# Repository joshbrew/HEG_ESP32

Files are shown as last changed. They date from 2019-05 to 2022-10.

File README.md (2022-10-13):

# HEG ESP32 - Open Source. Home of HEGduino!
Hemoencephalography meets highly affordable IoT! Now with WiFi and bluetooth! Incoming schematics, apps, and how-to's. [New Delobotomizer repo here](https://github.com/moothyknight/HEG_ESP32_Delobotomizer) for drivers for the new hardware.

Find the new, vastly easier to assembly HEGduino_V0 (3 parts, <10 dollars): https://github.com/joshbrew/hegduino_v0

Important HEGduino stuff you can find here:
- [HEG Training Quick Start Guide](https://github.com/moothyknight/HEG_ESP32/blob/master/Guides/HEG%20Training%20Quick%20Start%20Guide.pdf)
- [Progressive webapp (WIP) for Desktop or Android. Use with Chrome for now](https://hegalomania.netlify.app)
- [HEGduino Assembly](https://github.com/moothyknight/HEG_ESP32/blob/master/Guides/HEGduino%20Assembly%20Guide.pdf)
- [(For self-assembly only) Setting up Arduino to flash the ESP32 with our biofeedback software](https://github.com/moothyknight/HEG_ESP32/blob/master/Device_README.txt)
- [Updating the firmware via the web interface](https://github.com/moothyknight/HEG_ESP32/blob/master/Guides/How%20To%20Update.pdf)
- [Lolin32 Firmware and Updates](https://github.com/moothyknight/HEG_ESP32/tree/master/Device%20Drivers/HEG_WIFI_BLE_Lolin32)
- [Huzzah32 Feather Firmware and Updates](https://github.com/moothyknight/HEG_ESP32/tree/master/Device%20Drivers/HEG_WIFI_BLE_Feather)

## What is it?
Hemoencephalography is a single sensor FNIRS device meant to give a basic indication of cerebral blood flow changes in the brain.
Users then combine this indicator - the ratio of red to infrared light returned to the photodiode from the LEDs on your scalp or forehead - with simple visualization tools to help them increase or decrease metabolic/blood flow activity in the brain. 
This works like an odd form of physical therapy and is implicated as a powerful tool when combined in any brain health related therapies.

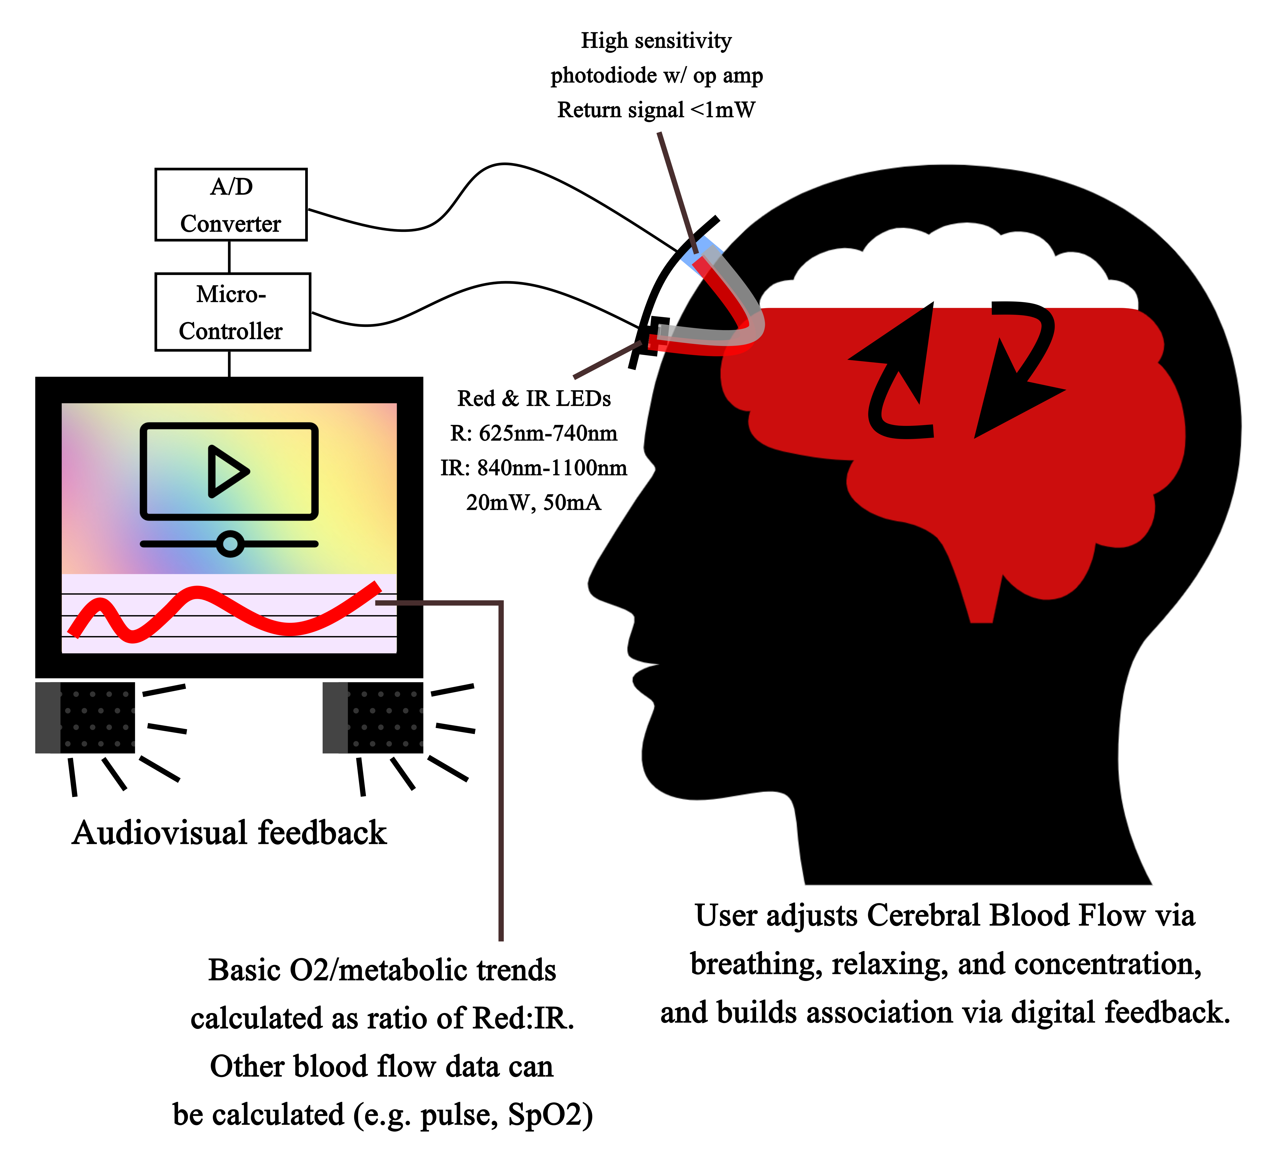
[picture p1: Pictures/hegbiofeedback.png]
Explanation


## Software

### Arduino Setup
See the [Device_Readme.txt](https://github.com/moothyknight/HEG_ESP32/blob/master/Device_README.txt)  for flashing instructions as well as available USB/WiFi/BLE commands and the changelog, including which dependencies are required for the Arduino IDE. We packaged the more minor dependencies in the Device_Drivers folder so you don't have to chase all of them down, just get Arduino and the ESP32 addon (github version) working.

Use the HEG_WIFI_BLE sketch in the arduino IDE on your respective ESP32. Pin definitions in HEG.h for the SDA/SCL and LEDs need to be adjusted according to your setup. 

These builds are tested on the Lolin32 and Huzzah32 Feather respectively but should work on any board after modifying the pinouts in HEG.h

### All Open Source Games, Tools, & APIs. See [the new PWA!](https://hegalomania.netlify.app)

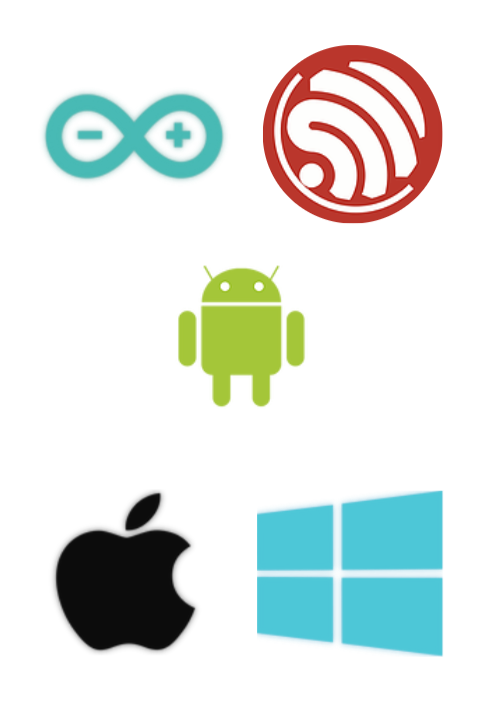
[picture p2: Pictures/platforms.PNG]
platforms


On the firmware you will find a Async Web Server with a cross-platform supported javascript app, enabling plug-and-play and global networking features. We are creating an open source combined therapy and research toolset, using the perks of an online-enabled device and all of the diverse tools available for web front and backend. This is a living project so stay tuned!

You can demo it now at a new mobile or desktop-installable webapp at [hegalomania.netlify.app](https://hegalomania.netlify.app). 

The USB support on the PWA is chrome-only until it is out of development for default web support. Install on desktop by opening the setting dropdown in Chrome (the 3 vertical dots in the top right of the browser) and click "Install HEG Alpha." It should be kept up to date automatically and work offline. Make sure you have the Earth textures on the Sunrise mode cached to use them offline, simply load them once to do this.  

It's evolving fast. We will eventually be comparable to professional BCI software, free of charge. In the More folder, please find the DataCharting.html applet for analyzing and comparing your data with interactive charts.

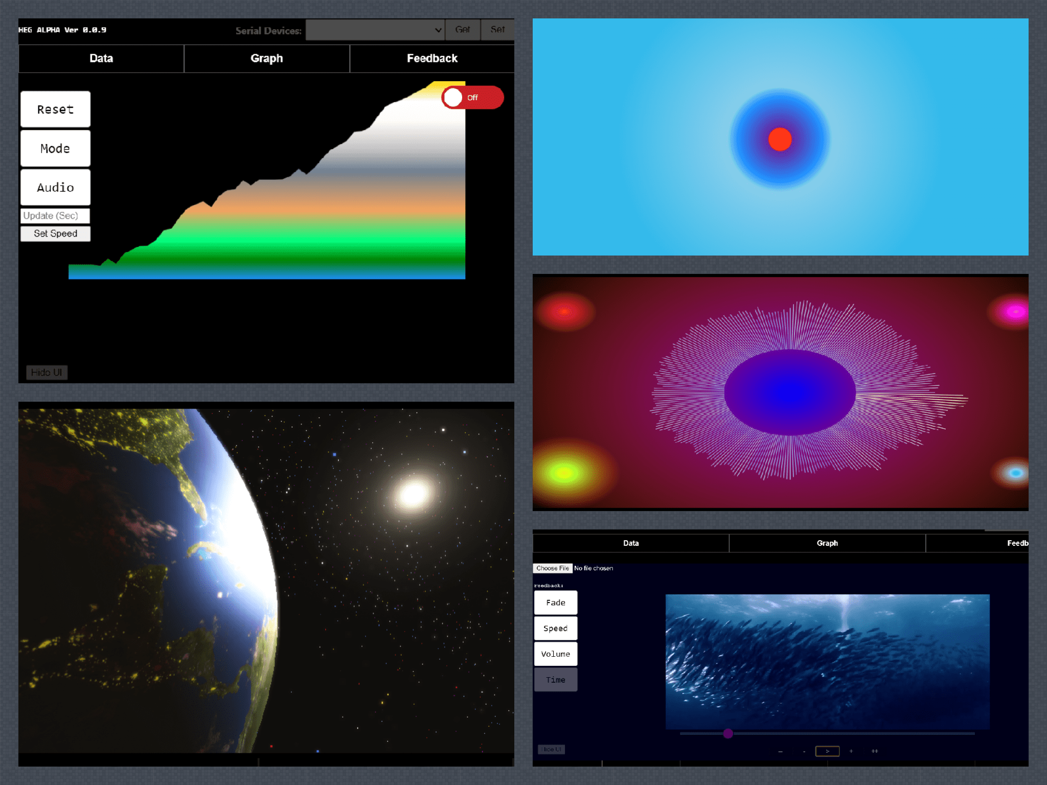
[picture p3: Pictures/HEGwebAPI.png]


## Data Charter (To be replaced) CSV analyzer for the web app (also found on our [Data page on our website](https://hegalpha.com))
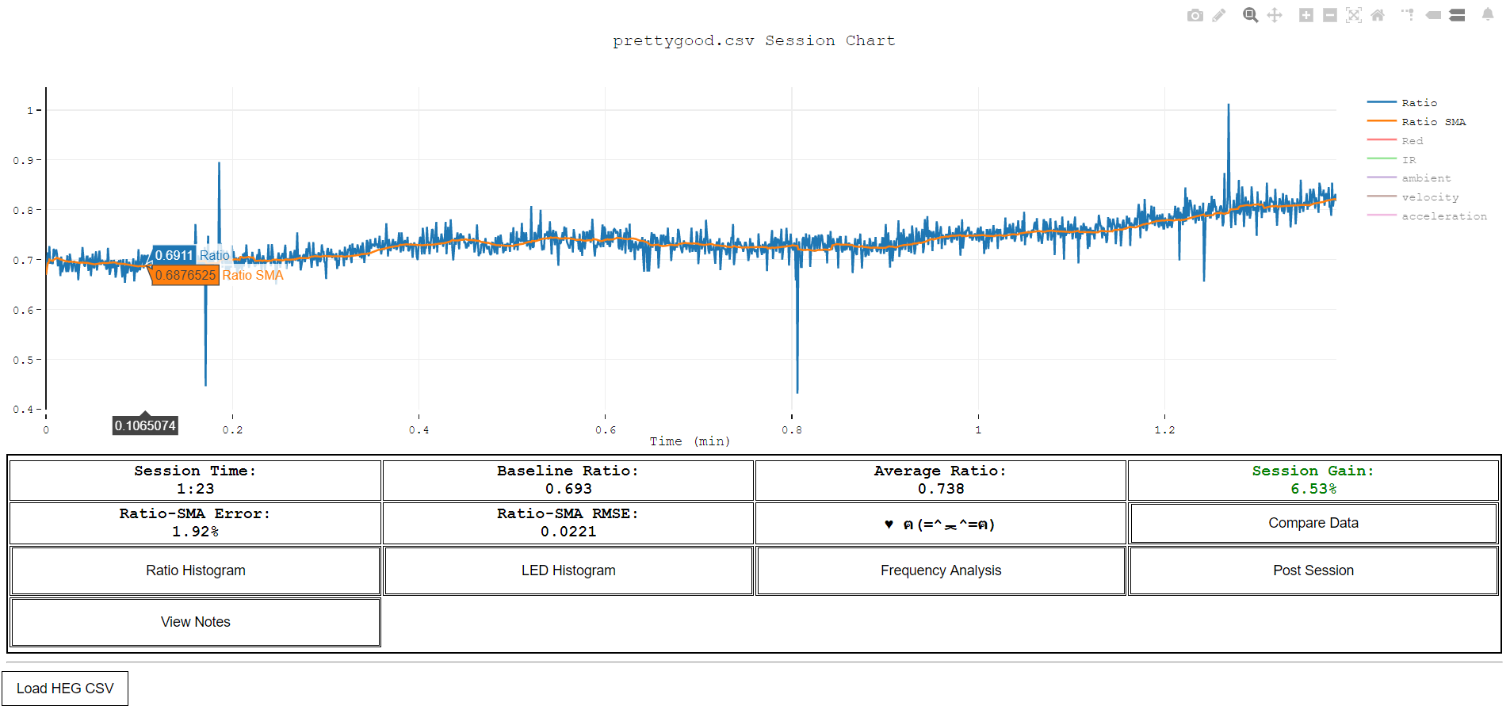
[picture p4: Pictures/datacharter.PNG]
HEGCharter


## More Links
Our website: [HEG Alpha](https://hegalpha.com)

Find us on [CrowdSupply](https://crowdsupply.com/alaskit/hegduino)

and [OpenBCI](https://shop.openbci.com/collections/frontpage/products/hegduino-kit?variant=32052268531784)

Special thanks to the [Biocomp/Biofeedback Institute of LA](https://www.biocompresearch.org/), [Brain Trainer](https://brain-trainer.com/), and [AlasKit](https://alaskit.net)

See also (very deprecated):
[Arduino Nano V3 HEG](https://github.com/moothyknight/HEG_Arduino)

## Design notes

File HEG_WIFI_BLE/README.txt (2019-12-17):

HEG WiFi WIP implementation. 

*****TO FLASH THIS SKETCH*****

You need the github version of the Arduino ESP32 libraries, follow steps accordingly for your OS.

You need to change the partition scheme to "Minimal SPIFFS" in the Arduino Tools menu.

Required Libraries: 
Arduino ESP32 latest dev or official build via git
AsyncTCP 
ESPAsyncWebServer 
ADS1X15
ArduinoJson

*****
IMPORTANT STEP
In Documents/Arduino/hardware/espressif/esp32/cores/esp32, open main.cpp and change 
xTaskCreateUniversal(loopTask, "loopTask", 8196, NULL, 1, &loopTaskHandle, CONFIG_ARDUINO_RUNNING_CORE);
to
xTaskCreateUniversal(loopTask, "loopTask", 16384, NULL, 1, &loopTaskHandle, CONFIG_ARDUINO_RUNNING_CORE);
The heap memory needs to be increased as the change in wifi can be too much on for the default arduino config. 
*****

After flashing this sketch onto the ESP32, you will find the new wifi
access point at the SSID: My_HEG with password: 12345678.

After logging into the access point, access the interface at 192.168.4.1

********************************

**
Optional - to have increased SPIFFs:

Arduino's default partition settings for the ESP32 need to be changed. A shell script has been provided to speed this up.

In the Arduino>hardware>espressif>esp32 folder replace boards.txt with the one in this library

In esp32>tools>partitions replace default.csv with the one in this library

These change the default partitioning to allow sketches up to 2MB in size on the ESP32 to make room for dual WiFi and BLE.

Extra SPIFFS notes:
You need the SPIFFs tools: https://github.com/me-no-dev/arduino-esp32fs-plugin
You also need to copy the esptool and mkspiffs EXE files in Arduino/hardware/espressif/esp32/tools/esptool and .../tools/mkspiffs into the
upper .../tools directory so the SPIFFs tool can find them.
**

--DEVICE INSTRUCTIONS--

HEG serial commands:
't' - Turns sensor on, you'll see a data stream if the sensor is isolated, as in contacting your skin and not exposed to ambient light.
'f' - Sensor off.
'W' - Reset WiFi to default access point mode (wipes saved credentials).
'b' - Toggle BLE mode, this resets the device to start in BLE mode, so you have to enter 'b' again through the serial or BLE connection to switch back to WiFi.
'R' - hard resets the ESP32.
's' - soft resets the sensor data.
'u' - toggles USB data stream. 
'p' - really basic pIR setting. Just turns the LEDs off as the photodiode picks up radiant heat from your body.
'0','1','2','3' - Changes ADC channel the device reads, in the case of multiple light sensors.
'5' - Read differential between A0 and A1 on ADS1115 to reduce noise (e.g. connect A1 to signal ground).
'6' - Read differential between A2 and A3 on ADS1115.
'D' - toggles ADC debugging (serial only).
'L' - toggles LED ambient light cancellation .
'T' - LED/PD test function. Not finished, easier to just check the 't' output real quick.
//'A' - BUGGED - toggles ADC error catching (if experiencing major fluctuations in data)

With extra sensors:
'l' - toggles sensor 0 and LED set 0.
'c' - toggles sensor 0 and LED set 2.
'r' - toggles sensor 1 and LED set 3.
'n' - broken and basic noise reduction implementation, where two LED sites are compared. This is not a good implementation yet, may cause device to hang.

Output data stream:

Current Milliseconds | Red LED Sample Average | IR LED Sample Average |
Red/IR Ratio Average | small Sav Lay Filter | large Sav Lay Filter |
adc Avg | position Average | ratio Slope | Attention Index

With noise average activated, the denoised ratio (if using an extra pair of LEDs) is inserted between Red/IR Ratio Avg and the small Sav Lay Filter.

The following demo pages are available:
/       - Index page, basic site navigation.
/sc     - State Changer demo page.
/listen - HEG Output event listener test. Better than websockets for this use case.
/connect - connect HEG to router so it may be accessed via a router instead. 
/update - Upload compiled binaries and flash the ESP32 over the web.

-------

Wifi code notes:

Use the /connect page to save Wifi credentials to EEPROM. The ESP32 will reset and attempt connection. 
If connection fails, the access point opens (StateChanger in your WiFi scanner).

BLE and WiFi do not work concurrently at the moment, logging into WiFi with BLE enabled may cause the ESP32 to crash.
Use the serial 'b' command for now to test switching modes or use the /connect page options.

mDNS should allow the ESP32 to be accessed via http://esp32.local. It requires Bonjour service enabled. I have not had success yet, but it works on Apple systems apparently.

-------

Serial Port notes:
Chrome app serial monitor (alternative to Arduino): https://chrome.google.com/webstore/detail/serial-monitor/ohncdkkhephpakbbecnkclhjkmbjnmlo/related?hl=en
Arduino IDE has a debugger that comes with the ESP32 libs if there are some weird crashes happening.
-------

HEG Code notes:

The noise_reduce() function in this version is still broken. That needs to be triggered.

On the /listen or /stream page once the event listener/websocket is connected you can control and test the HEG through the Serial monitor. Right now there is a manual 75ms delay on the data stream, I'm going to create buffers as the new sensors will be WAY faster than TCP can handle.

*-*-*-*-*-*-*
Changelog:
*-*-*-*-*-*-*
12/16/19
------
- updated front page, connection page, and help page. Now with version number visible on main page.
- the web API lets you set an arbitrary host for the event source now for quicker remote play (set host with a new HEGwebAPI(parentId,defaultUI,**hostIP**))
 
12/14/19
------
- Made standalone /api page with uninitialized JS api and CSS available for external use.

12/10/19
------
- Rolled back ADC library due to too much instability.

12/8/19
------
- Fixed sampling issues. Now doing 3 samples per LED (and ambient) for 20sps solid over USB, WiFi, and BLE.
- Fixed BLE (thanks Diego!)

12/3/19
------
- Changed ADS1115 libraries to the addicore version (via on i2cdevlib)
- Upped sample rate to 475sps, ratio rate (with ambient cancellation) should now be ~133 at full speed over Serial.
- Fixed Serial commands not being responsive
- Removed "T" test command for now.

11/25/19
------
- fix LEDs not shutting off when pausing HEG
- lowered power consumption
- fixed circleJS in web API

Known bugs:
- Serial USB commands don't register very well 
- ADC anomalies with WiFi (probably power consumption related)
- xOffset bugged when changing xScale and xOffset together

To Do:
- Use a better ADS1115 lib to improve speed
- Web Demo CSS and functionality improvements
- IE and Edge can't find the HEGwebAPI.js script (this is likely the same issue on mobile)

11/11/19
------
- fix web api and hegstudio to match changes

11/9/19
------
- removed sav lay filter (do it on front end instead after checking data)

11/4/19
------
- ADC error check in HEG.h (to deal with a webserver bug), use 'A' to toggle. 
- Add progress events for /update page.

KNOWN BUGS:
The error checker can cause hangups and overheat the chip, don't use it yet

11/3/19
------
-webDemo now filters bad data out for a smoother experience, to compensate for a bug mainly
-testing threading to try to fix wifi data streaming errors. Turn sensor off and on if connecting online while sensor is active. (very particular not often-gonna-happen bug)

Known bugs:
The wifi connection causes errors in the ADC readings for some reason, need to fix this
to make the sav lay filters usable over web.

10/29/19
------
-/discovery page for testing device scanning from mobile
-Reimplemented ambient noise cancelling and added a read_differential mode. Works much better like this, closer to the original!
-/help page (BIG work in progress)

10/21/19
------
-connect page now has a suggest IP option. Return to the /connect page after reconnecting to the access point.
If it works correctly you get booted to the main page and can go straight to the /connect page again, scroll down, and see the suggested info above the wifi scan text.
-proof of concept hill climb game
-more cleanup (not all the way there yet)

More to do:
Audio mode that just plays a tone that gets louder or quieter? 
Device search on local wifi when in STA mode.
More controls for modes.

10/18/19
------
-integrated audio mode
-added volume feedback for video option
-code feng shui improvements

FYI: not all buttons hooked up yet

Known bugs:
-not every browser works on canvas demo
-poor audio quality on visualizer mode - try manual buffering. Bug not present in standalone visualizer.
-offset button bugged when offsetting more than the number of graph vertices (look at xoffsetSlider.onclick setting)
10/17/19
------
smooth mode switching on demo page. Audio and hill climbing (LIFE game re-creation) games incoming.
change graph to show cumulative SMA 1s - 2s slope changes. This math is a simple noise filter that is still reactive to the current information, which can overcome noise issues. 
split code up into multiple files to fit a cleaner traditional webapp format.
web api improving and generalizing rapidly
can set primary/secondary dns if needed, smart config type stuff incoming.

couple bugs:
X offset slider still, it's 3 lines of code causing a problem.
the replay function works fine but goes over the index when resetting the data. This bit will be re-done as the code is spaghetti.

10/14/19
------
-x offset bar. Has a bug when offsetting when graph scale is lower than the array being sliced. page has to be reloaded if red line vanishes.
-Even classier, almost finished streamlining code.
-integrated hegvid code with main page, need to create options to swap once finished generalizing the data handling. this will be smoooooth

10/13/19
------
webGL graphing API improvements. More to come.
WIP Object-oriented web API on canvas demo page. Final suite will be completely class-based.
Sensitivity slider.
/hegvid -> /video (this page will be integrated with the main demo)

More TODO:
Audio visualizer (HTML5 has sweet built-in tools)
CSS Overhaul w/ animations. Utilize webkit/moz/mobile libs.
Fix mobile support for web demo (mostly requires permissions changes)

10/11/19
-----
/hegvid page improvements/experiments. Can load local video files (web URLs next, some site embedding like Vimeo MIGHT work)

10/10/19
-----
CSV Save/Load functions added.
Graphing improved, canvas demo fairly playable now. 
Waiting on new pcbs to get definitive data after fixing noise issues in designs.
GraphJS wrapper class for graphing.

TODO:
graph upgrades
reformat functions and variables into respective classes to reduce bloat.
sliders for exploring data
create SPIFFS js packages? That way we can break up essential functions on the webAPI and reduce bloat or add third party packages easily.
hegstudio brightness exercise recreation is easiest to do with default <video> tag and a transparency overlay.
Fix spaghetti

10/6/19
-----
Fixed crash when changing wifi modes
Add static IP settings. 
Working on WebGL based graphing and video controls. /hegvid wip

10/1/19
------
Canvas demo
Really basic navigation on index page
Fix websocket page to use js to call the hostname in case of esp32.local being used.
More POST commands, also added text input-based command method as an option, only send single char.

9/9/19
------
EventSource works great!

More TODO:
Make connect page notify the user of the new IP address if esp32.local is not fixed.
Convert websockets to drive commandESP32

9/5/19
------
TODO:
Data visualizer. HEG Life game in canvas?
Stress testing - try EventSource instead of Websockets. Websockets can overflow and crash the ESP32 easily if there is lag clientside.
Login interface?
HTML interface to use commandESP32

9/5/2019
------
Fixed OTA, update boards.txt and default.csv in their respective folders (see above install instructions)
Changed setup loop so wifi is always chosen if EEPROM.read(0) is not 1 for BLE.

9/3/19
------
Included BLE support. toggle BLE/WIFI with 'b', BLE default off due to conflict with WiFi
Websockets and HEG now on separate threads so sensor speed is not impacted - WS speed set at 13.33 updates/sec as it's stable. Max = 16/sec
/update broken. Gotta fix it.
Lots of housekeeping to keep workflow easy, tested the freeRTOS threading system a ton.
commandESP32 now in WiFi_API.h.

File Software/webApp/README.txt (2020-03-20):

Step 1: Connect to your HEG WiFi
Step 2: Open webDemo.html (preferably with Chrome, Firefox, Edge Beta, or Brave) and open the Data menu
Step 3: Click "Connect" to connect to 192.168.4.1 or enter a custom IP if you are connected through a network.
Step 4: Press start! You should see your device come on!

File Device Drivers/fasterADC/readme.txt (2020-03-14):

You can replace your HEG.h and WiFi_API.h with these as well as add the library to your Arduino Libraries folder.

To get the ADS1115 library working (use the addicore version on github), you must also have the I2C device library by jrwoberg.
For Arduino, you must drag the files "I2Cdev.cpp" and "I2Cdev.h" from i2cdevlib-master/Arduino/I2Cdev to the main i2cdevlib-master folder so Arduino can find it.

In I2Cdev.cpp you must add these lines just after #include "I2Cdev.h" at the top:

#ifdef ARDUINO_ARCH_ESP32
    #define BUFFER_LENGTH I2C_BUFFER_LENGTH
#endif

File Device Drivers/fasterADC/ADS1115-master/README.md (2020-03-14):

# ADS1115
Arduino library for the ADS1115 Analog-to-Digital Converter

## Original Repository:
From https://github.com/jrowberg/i2cdevlib

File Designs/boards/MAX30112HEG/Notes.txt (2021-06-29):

I couldn't get this to turn on when I tried making it, but the SPI regulator was placed backwards. It should work.
Find WIP Arduino drivers at: https://github.com/moothyknight/MAX30112_Arduino

Notes: LDO and logic leveling could be lower noise.

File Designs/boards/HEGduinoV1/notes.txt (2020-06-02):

V1.1 WIP design, main goal trying to figure out how to squash the noise because 2 years in and I'm still a totally n00b circuit designer.

The noise sources:
- Power
  -- e.g. wired connections
  -- ESP32 power draw (e.g. can lower power consumption in settings)
- WiFi
  -- e.g. during transactions
  -- I obviously shouldn't have the ADC right underneath but copper ought to help absorb WiFi inductance. I can get to very low noise even on WiFi, even on a 10ft wire to the sensor...
- Grounding
  -- Keeping analog and digital grounds as far away from each other as possible.

Things I'm doing:
- For one, fixing my terrible wiring on the V1.0 (result of not starting from scratch from my old old drafts). E.g. unnecessary vias, digital SDA/SCL and AVDD pins the same (may cause issues).
- Alternative LDO for analog power source to ADC and to OPT101. Includes a few caps.
- Moving around grounding stuff, different ground plane strategy (I forgot to even attach the last ones to the pins).

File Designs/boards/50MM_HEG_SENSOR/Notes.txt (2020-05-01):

Photodiodes need an amplifier circuit or an ADC that's tailored for these (e.g. the MAX30112 or MAX8614X). 
For general purpose ADCs use OPT101 or similar with built in amps.

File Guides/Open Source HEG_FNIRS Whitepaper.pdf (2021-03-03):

Joshua Brewster
October 2020

## Open Source, Low Cost, Scalable fNIRS/HEG Whitepaper

Contents

Abstract | 2
Acronyms | 2
FNIRS Overview | 3
HEG Biofeedback Overview | 9
List of HEG Case Studies | 17
HEG Alpha | 18
Citations from Hyperlinks | 24

Abstract:
This whitepaper is to cover what I’ve learned from functional Near Infrared Spectroscopy (fNIRS) and Hemoencephalography (HEG) biofeedback as well as my development progress on open source low cost tools for anyone to jump into this space and benefit from it either for education or home therapy. These are important emerging imaging and therapeutic technologies as they offer a low cost and low abstraction method to work with live or recorded information from the brain. This is paired with a type of brain blood flow training for biofeedback therapy that allows users to increase their baseline brain perfusion in their prefrontal cortex and beyond. This field promises even more interesting monitoring methods and psychiatric tools akin to functional Magnetic Resonance Imaging (fMRI) with the use of tomography (DOT), laser interferometry (OCT), and deep learning feature decoders to understand brain activity. Our goal is to carve a path for open source efforts in this area by developing low cost tools and free software through reproducing different public domain hardware and experiments. We are sharing working and tested plans free, and hardware low cost.

Acronyms:
fNIRS - Functional Near Infrared Spectroscopy HEG - Hemoencephalography
EEG - Electroencephalography
HbO2 - Oxygenated Hemoglobin
Hb - Deoxygenated Hemoglobin SpO2 - Pulsatile Oxygen Saturation
CBF - Cerebral Blood Flow
DOT - Diffuse Optical Tomography
fMRI - Functional Magnetic Resonance Imaging OCT - Optical Coherence Tomography

fNIRS overview:

Here will give a brief overview of the essential concepts of Functional Near Infrared Spectroscopy (fNIRS) and brain blood flow biofeedback. The Hemoencephalography (HEG) device is simply a single sensor fNIRS device with red and infrared wavelengths standard to pulse oximetry, and 3 cm spacing for depth readings. Alternatively it has been done with thermocouples to just measure IR radiation off your forehead, while photodiodes also include optical wavelengths. You can view the original patent 5995857 by Hershel Toomim and Bob Marsh, now public domain, online. (https://patents.google.com/patent/US5995857A/en)

fNIRS is the application of near infrared light, and more generally optical wavelengths, for the purpose of imaging the surface of the brain and monitoring Cerebral Blood Flow (CBF). It is much cheaper but not as complete as a functional Magnetic Resonance Imaging (fMRI) scan with tracer injections, though it can still elucidate a ton of useful structural and functional data about the brain. The skull is highly translucent and even lends itself well for optical imaging of the brain. This is accomplished by placing LED or laser emitters with specific wavelengths at specific distances from photosensors on the scalp or forehead and flashing them repeatedly while reading the response on the photodiode. Your pulse for example is plainly visible by this method and blood oxygen can be calculated.

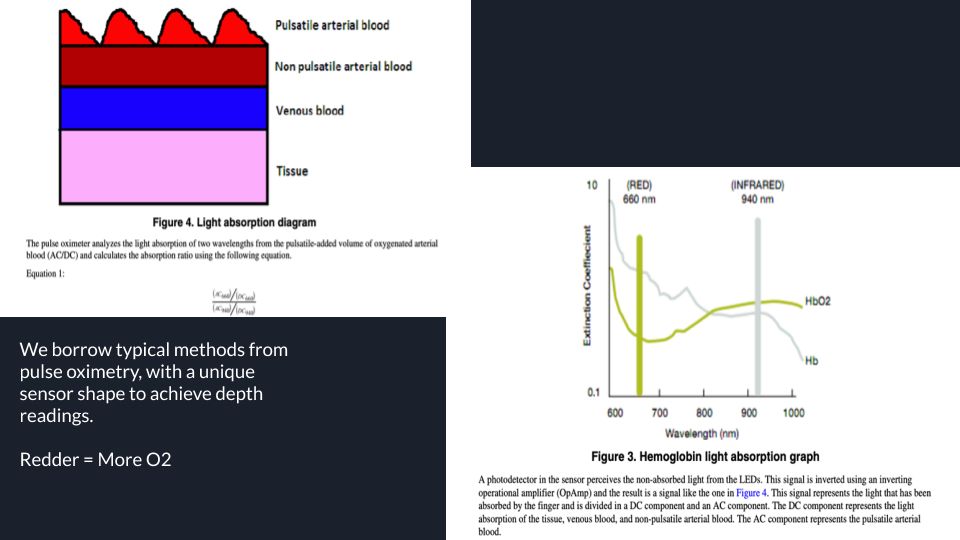
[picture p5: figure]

Optical wavelengths between Green - usually Red or Far Red - and Near-Infrared are generally chosen, one above 810nm and one below as Hb and HbO2 have opposing absorption indexes above and below that point, and are identical at that point. This creates a relationship that can be used to empirically calculate oxygen saturation and monitor blood flow. Pulse oximeters are probably the most universal application of fNIRS used for skin surface or fingertip pulse and pulsatile oxygen (SpO2) measurement.

This goes much further, however, as some optical wavelengths have deeper penetration than others, peaking apparently at 1064nm (https://www.spiedigitallibrary.org/journals/journal-of-biomedical-optics/volume-25/issue-09/097003/Diffuse-correlation-spectroscopy-measurements-of-blood-flow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) in the Near-Infrared spectrum. Photodiode and emitter pairs can even be densely arrayed to enable image reconstruction, and the curvature of the skull allows estimation of light paths between source and sensor pairs to perform 2D or 3D reconstruction using techniques similarly seen in geological surveying or electrical tomography. With mapping techniques especially demonstrated by a little-known piece of tech called Diffuse Optical Tomography (DOT), we can begin to functionally image the brain and spatially monitor metabolic and blood flow activity.

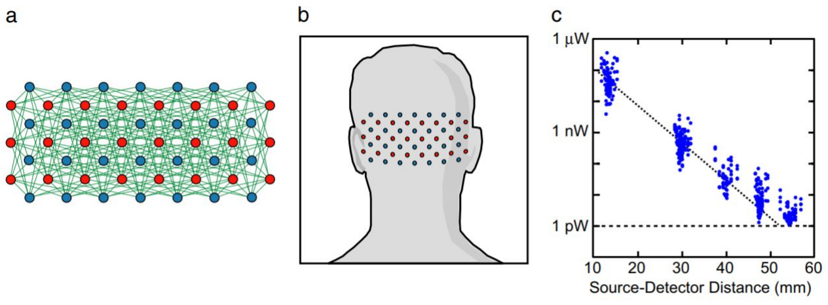
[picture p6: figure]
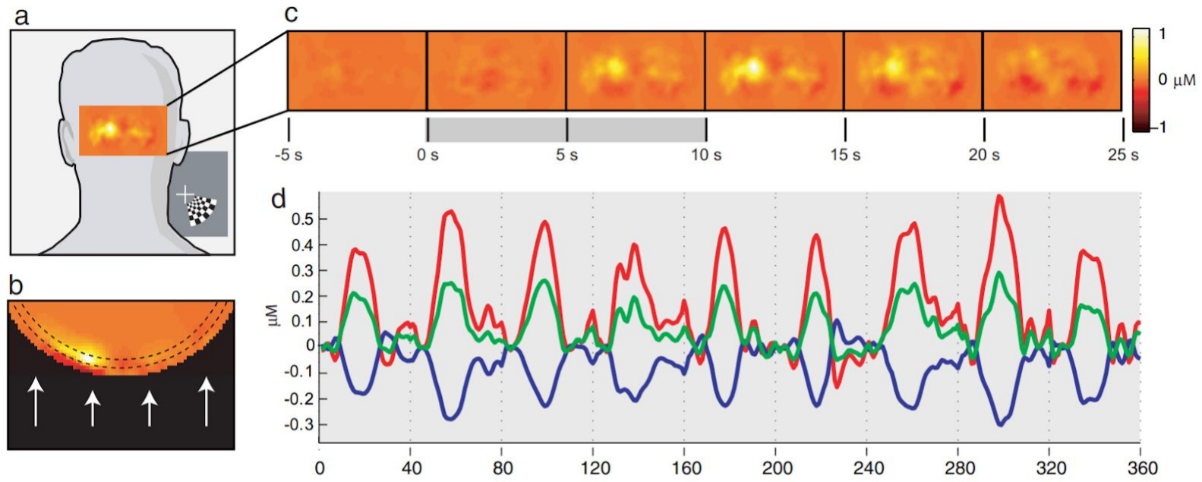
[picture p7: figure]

Source: Retinotopic mapping of adult human visual cortex with high-density dif use optical tomography (https://www.pnas.org/content/104/29/12169)
- Ben Zef , Brian White, Hamid Deghani, Bradley Schlagger, Joseph Culver (2007)

In the above image you can clearly see the two hemispheres of the visual cortex activating using only 28 sensors and 24 emitter pairs in the near-infrared range. My favorite study involving fMRI data made deep learning-assisted reconstructions of images and videos from visual cortex activation patterns as seen in the next image, which ideally can be accomplished using fNIRS. In the next image you can see how deep learning of fMRI activity gets vaguely close to what the person was looking at, and that’s spooky enough. There are other impressive studies (https://news.berkeley.edu/2011/09/22/brain-movies/) out there involving similar data for doing video reconstruction from the visual cortex.

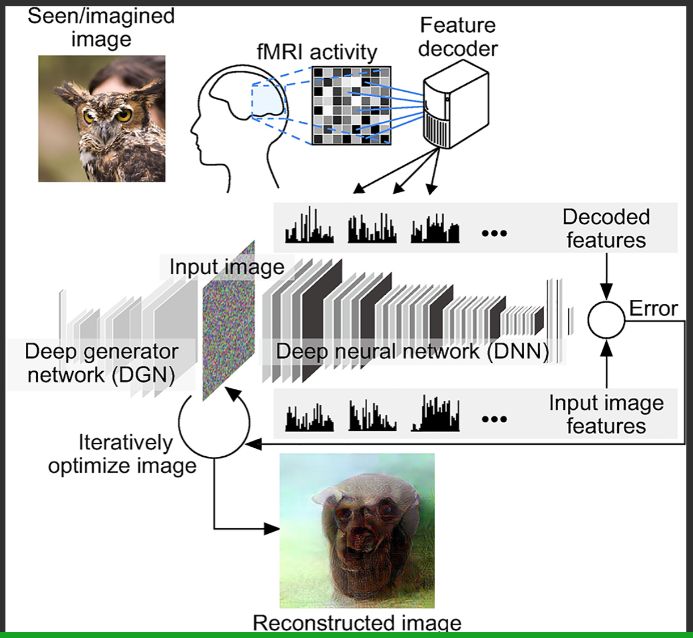
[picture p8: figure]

Source: Deep image reconstruction from human brain activity (https://journals.plos.org/ploscompbiol/article?id=10.1371/journal.pcbi.1006633) - Guohua Shen, Tomoyasu Horikawa, Kei Majima, Yukiyasu Kamitani (2017)

This deep image reconstruction technique gets more interesting the more you look:

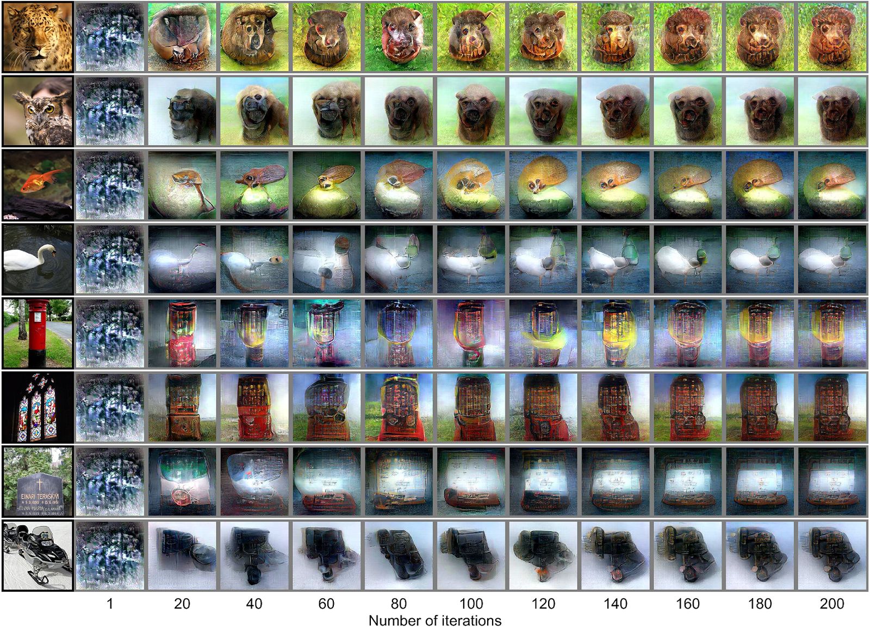
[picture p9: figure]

Source: Deep image reconstruction from human brain activity (https://journals.plos.org/ploscompbiol/article?id=10.1371/journal.pcbi.1006633) - Guohua Shen, Tomoyasu Horikawa, Kei Majima, Yukiyasu Kamitani (2017)

Even rough information can lead to fairly accurate categorizations by deep learning networks, which are picking signal out of noise and comparing it to a learned image database. What is striking to me, when paying special attention to the church window reconstruction in the above image, is that the visual cortex may also blend that image with categorical archetypes encoded within the visual cortex. The church window gets painted onto an obelisk in a grassy field from the looks of it, and to me that suggests Jungian-like object archetypes existing within our sensory processing field when chunking visual input or any sensory input for that matter, likely for efficiency. It’s a weird but not an original idea. This can be related to a recent publication (https://github.com/poloclub/cnn-explainer) looking at how convolutional neural networks (CNNs) encode different categories into its neurons by visualizing what those neuron ensembles actually encoded - where CNNs are heavily based off of the structure of the human visual cortex:

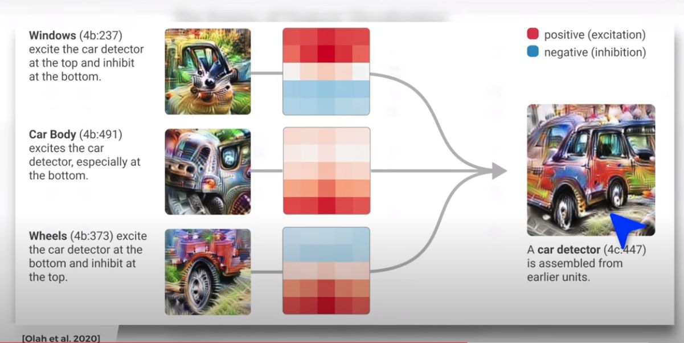
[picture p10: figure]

Source: CNN Explainer: Learning Convolutional Neural Networks with Interactive Visualization. (https://arxiv.org/abs/2004.15004) Wang, Zijie J., Robert Turko, Omar Shaikh, Haekyu Park, Nilaksh Das, Fred Hohman, Minsuk Kahng, and Duen Horng Chau. (2020)

You can see how the different parts of the car get encoded as amalgams of different labeled feature sets that look like trippy fractal meta images, representing all of the different images exposed to the neural network during training. This all suggests a powerful imaging tool for gaining some much deeper insights into human visuospatial psychology and more by live decoding the brain’s actual activity, though that’s pretty far out, dude. Using machine learning decoding comes with a lot of potential confirmation bias problems, too.

“What we call ‘reality,’ consists of an elaborate papier-mâché construction of imagination and theory filled in between a few iron posts of observation.” - Donald Hoffman (https://www.youtube.com/watch?v=3MvGGjcTEpQ) in The Case Against Reality: Why Evolution Hid the Truth from our Eyes

This is just what’s possible with diffuse optical imaging or Fast Optical Signal (https://www.ncbi.nlm.nih.gov/books/NBK20223/) spatial mapping by another name, and uses a lot of mathemagic to make it happen. It is also constrained by the speed of your processing and LED routines, and sensor array density. A commercial example of this is the NIRSIT device for frontal lobe monitoring with around 200 overlapping sensors on the forehead. So what about modern laser scanning tech? This leads to even more interesting but much more difficult infrared imaging featuring interferometry. This is best demonstrated using Optical Coherence

Tomography (OCT), where you apply the similar fNIRS principles to microscopy and get freaky with mirrors, beam splitters. and interferograms.

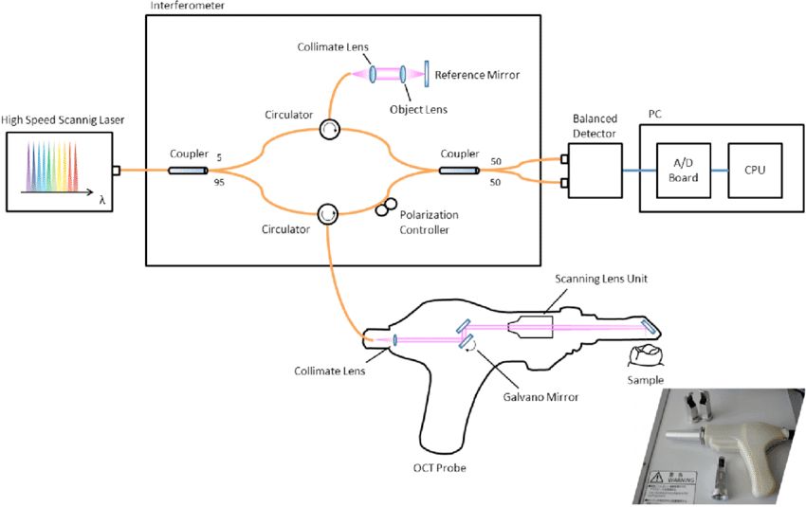
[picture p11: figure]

Source: Assessment of natural enamel lesions with optical coherence tomography in comparison with microfocus X-ray computed tomography (https://pubmed.ncbi.nlm.nih.gov/26158079/) - Espigaras et. al. (2015)

OCT provides another level of optical imaging and is currently only used for microscopic applications, requiring very high coherence lasers and lenses and other expensive optical equipment. This is able to perform miracles like high res 3D fingerprint detection or 3D angiography to image dense capillary networks, and more. A couple main applications are in eye clinics to look for issues in your cornea layers or experimentally in high security zones for extra fingerprint verification.

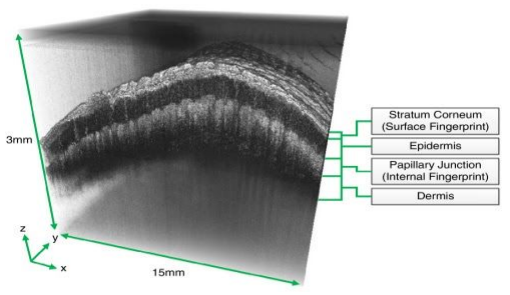
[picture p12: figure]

Source: Automated spoof-detection for fingerprints using optical coherence tomography (https://www.researchgate.net/publication/301745082_Automated_spoof-detection_for_fingerprints_using_optical_coherence_tomography) - Luke Nicholas Darlow, Leandra Webb, Natasha Botha (2016)

And who said modern science isn’t cool enough? This of course comes on the heels of massively improved manufacturing techniques and computer technology which can handle the high resolution and high processing speeds required for this 3D microscopy. What if you can scale this up, however, to effectively create a much higher resolution DOT image that is halfway in-between the high resolution microscopy and the rough 28 sensor DOT image (which still highlights brain hemispheres and some gyrations as seen above)? This has many engineering challenges associated, but it probably can be done. This would improve resolution especially at deeper layers, and can be enhanced even further with the use of dynamic focus (https://pubmed.ncbi.nlm.nih.gov/26662065/) and more tricks from RF and astronomy.

HEG Biofeedback Overview

First, familiarize yourself with various Cerebral Blood Flow (CBF) studies in this informal list, which demonstrate how different physical and psychological stresses, not to mention aging, have significant impacts on CBF. This helps stage an argument for why therapies targeting this process may be so significant to improving overall wellbeing:

Perfusion MRI to study CBF under psychological stress - Wang et. al. https://www.pnas.org/content/102/49/17804.short

Cerebral Blood Flow changes in socially phobic people during stressful speaking tasks - Tillfors et. al. https://ajp.psychiatryonline.org/doi/full/10.1176/appi.ajp.158.8.1220

CBF changes in cops with PTSD - Lindauer et. al. https://www.sciencedirect.com/science/article/abs/pii/S0006322304008546

Cerebral Hypoperfusion in migraine patients - Woods et. al. https://www.nejm.org/doi/full/10.1056/NEJM199412223312505

Cerebral Hypoperfusion and the onset of dementia - Ruitenberg et. al. https://onlinelibrary.wiley.com/doi/abs/10.1002/ana.20493

Cerebral Hypoperfusion in children with dysphasia and ADD - Lou et. al. https://jamanetwork.com/journals/jamaneurology/article-abstract/583298

Cerebral Hypoperfusion accelerates Alzheimer's - Okamoto et. al. https://link.springer.com/article/10.1007/s00401-011-0925-9

Effects of Aging on Cerebral Blood Flow - Ances et. al. https://onlinelibrary.wiley.com/doi/full/10.1002/hbm.20574

Sympathetic nervous system effects on CBF - Seifert et. al. https://www.ncbi.nlm.nih.gov/pubmed/21963551

Cognitive training to improve resting Cerebral Blood Flow in the PFC in adults - Mozolic et. al. https://www.frontiersin.org/articles/10.3389/neuro.09.016.2010/full

Exercise increases CBF, NIRS study - Ide and Secher https://www.sciencedirect.com/science/article/pii/S030100829900057X

CBF changes with volitional breathing - Colebatch et. al. https://physoc.onlinelibrary.wiley.com/doi/abs/10.1113/jphysiol.1991.sp018824

Tasty-looking food increases cerebral blood flow - Koyama et. al. https://www.tandfonline.com/doi/abs/10.3109/09637486.2015.1118618

What makes the HEG device special and rather unorthodox is that it’s a purposefully stripped down tool meant to capture general rises and falls in blood oxygen and the corresponding metabolic action in the targeted area of your brain. Breathing patterns for example are fairly clear, as well as when the user is paying attention or stressed out. These are all clearly marked by slow or even rapid changes in blood oxygen content in the prefrontal cortex. Increased activity corresponds with increased regional CBF when neurons draw on capillaries to meet their energy demands to fire. Compared to EEG the results are immediately apparent without any complex information processing required and happens slowly enough to be quite visible to the naked eye. This allows users to perform a type of brain exercise by breathing and paying attention to their thought patterns and seeing how prefrontal cortex oxygen saturation changes. Remember this is the same tech used for that cool imaging in the last section, just totally stripped down to remove any abstraction.

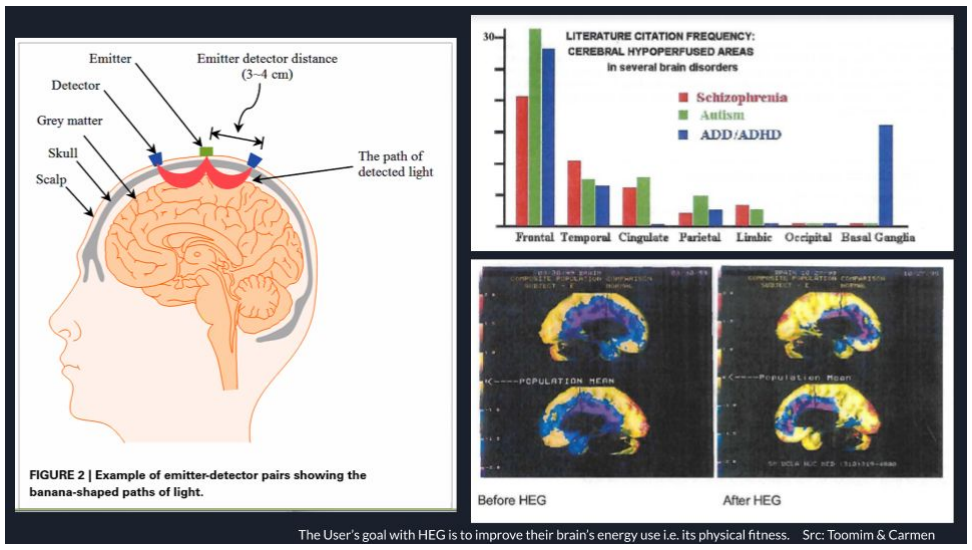
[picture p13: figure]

The Biofeedback Institute of LA had a few hundred SPECT scans performed on dozens of patients over several month periods while training with their HEG device several times per week. BILA noted how often issues like hypofrontality, i.e. reduced frontal lobe metabolism, show up in so many studies of mental disorders, and this therapy offered a direct remediation method quite unique to this technology. They recorded and reported fairly dramatic increases in average perfusion in the brain by population mean (see bottom right in the image above) after several months of HEG training.

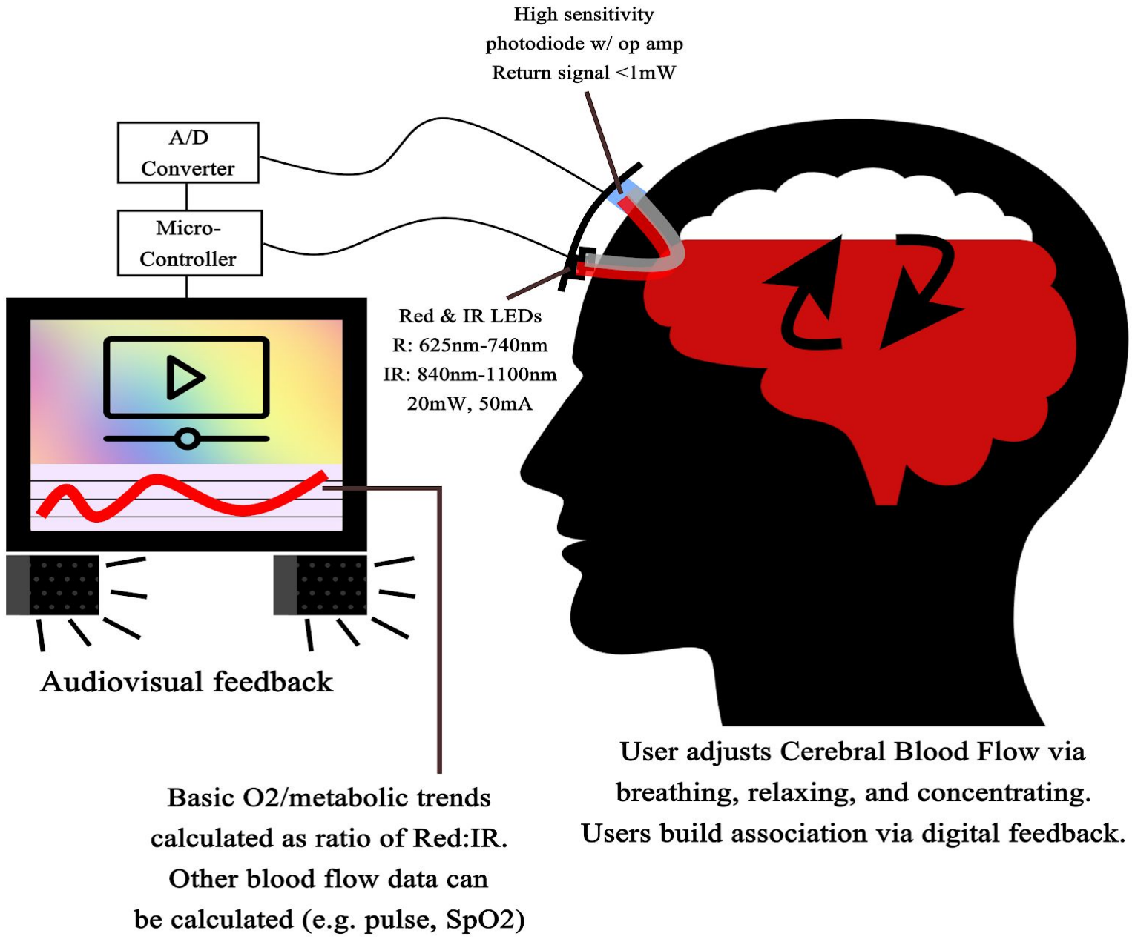
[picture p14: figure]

To begin to explain the breathing exercise’s effects, we need to talk about volitional breathing. Volitional breathing, i.e. controlled breathing, is a time-tested tactic to redirect oneself in the moment as well as strengthen one’s overall sense of clarity and presence. It’s obvious that optimal breathing patterns will enable better oxygen delivery and therefore bodily functioning, and different breathing styles can stress or relax the body in interesting ways as practiced by a lot of yogis or notably by Wim Hof. (https://en.wikipedia.org/wiki/Wim_Hof) Oh but there’s more to this story.

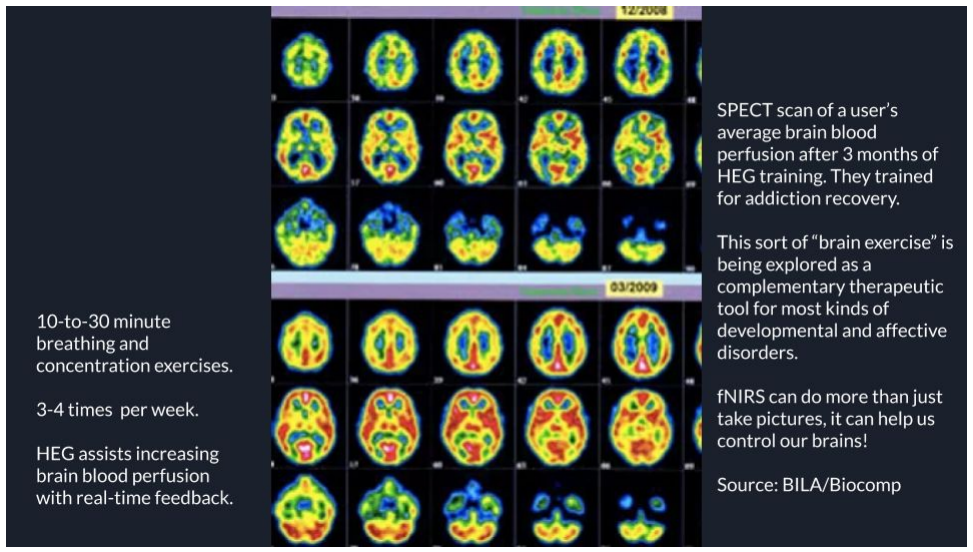
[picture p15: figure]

A 2018 study (https://journals.physiology.org/doi/full/10.1152/jn.00551.2017) with implantable EEG in a seizure patient found that the anterior cingulate cortex (ACC) would oscillate in correspondence with controlled breathing patterns then stop cohering nearly as much when automatically breathing. This shows that the ACC among many others is quite involved when controlling and paying attention to our breath, and this networks with the rest of our frontal lobe as well as plays important roles in regulating the limbic system - notably the amygdala. A 2018 mouse brain study (https://www.nature.com/articles/s41467-018-05090-y) in Nature magazine discovered that stimulating the ACC reduced instinctual fear responses due to its direct connection to the amygdala and other related areas for fear (same with the olfactory bulb). (https://www.nature.com/articles/s41467-018-03988-1) Lack of activity in the ACC conversely increased instinctual fear response. This helps demonstrate how the frontal cortex plays a role in inhibiting instinctive reactions, which is a well known idea. However, this corresponds with regions of the brain that we now know we have direct influence on via controlled breathing, with several other networks probed in the volitional breathing study also correlating to either controlling breathing and/or being aware of breathing.

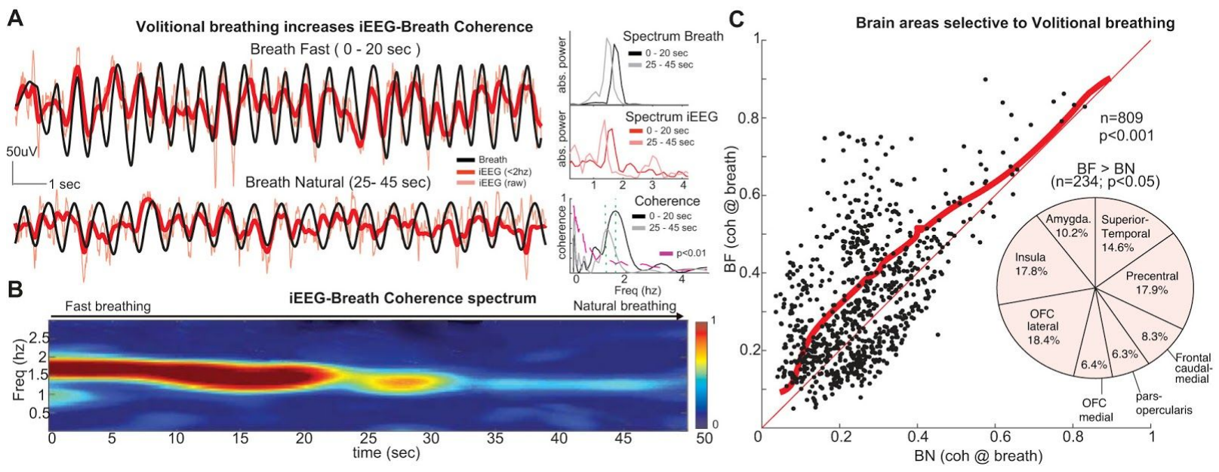
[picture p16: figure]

Source: Breathing above the brainstem: volitional control and attentional modulation in humans (https://journals.physiology.org/doi/full/10.1152/jn.00551.2017) - Jose Herrero, Simon Khuvis, Erin Yeagle, Moran Cerf, Ashesh Mehta (2018)

Now let’s talk about energy use for a minute and how stimulating the neocortex enables healthier cortical growth. This may help us understand why a direct brain stimulation method via controlled breathing may be so significant and help explain why it’s been such a long held practice. This is also how we can begin to establish the idea of “brain exercise” as a real thing and something with a lot of nuance and potential benefits along with technologically-assisted psychotherapy.

The brain directs energy where it needs. It’s like a water balloon with limited blood supply and it’s squeezing itself in different places to direct that blood supply to the most-needed areas so that they can operate, recover, and self-clean. Your brain also eats at least a steady 20% of the body’s resting state (https://www.ncbi.nlm.nih.gov/pmc/articles/PMC124895/)

calories (https://www.ncbi.nlm.nih.gov/pmc/articles/PMC124895/) or about 300 calories/day - making it the most high demand organ in your body when compared to body mass. Young children’s brains have been hypothesized to burn as high as 2/3rds (https://www.pnas.org/content/116/27/13266) of the body’s energy with all of the major growth the brain undergoes, making it that much more sensitive to changes in the developmental environment.

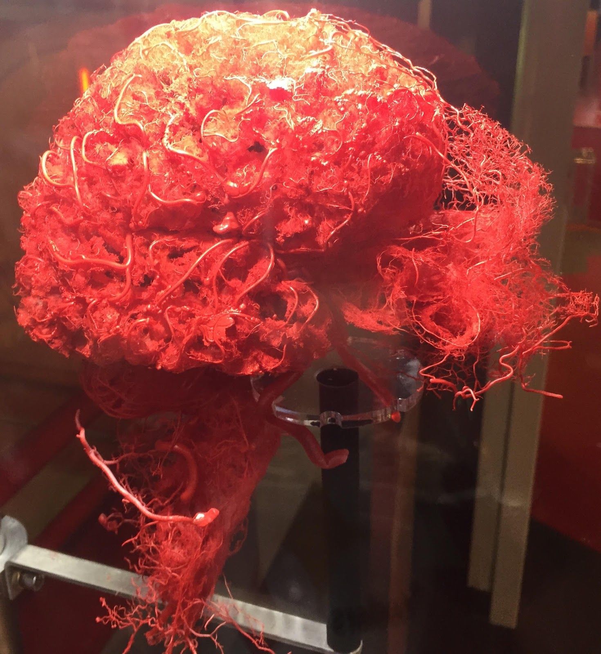
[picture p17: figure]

Human brain vascular system. Source: Carnegie Science Center in Pennsylvania

High demand means high vascularization (https://www.ncbi.nlm.nih.gov/pmc/articles/PMC4678116/) i.e. density of blood flow networks - a process managed by our glial and endothelial cells. Without that process, brain cells can’t grow, heal, or fire on demand, while the demand also encourages more vascularization by signaling capillaries to grow into the networks as part of the reinforcement process. Astrocytes (https://www.ncbi.nlm.nih.gov/pmc/articles/PMC6562853/) - which make metabolites and neurotransmitters for neurons, manage hundreds of thousands of synaptic clefts each, and help perform vasodilation - can be stimulated (https://www.nature.com/articles/s41467-019-13956-y) with diaphragmatic breathing (http://projects.hsl.wisc.edu/SERVICE/modules/12/M12_CT_ThePowerOfBreathDiaphragmaticBreathing.pdf) (a tried and true stress and anxiety relief technique) to regulate regional blood supply like a baroreceptor, and are another fundamental yet underrepresented (https://www.ncbi.nlm.nih.gov/pmc/articles/PMC6379461/) part of the brain’s processing. Exercise and stimulation also induces astrocyte plasticity (https://www.ncbi.nlm.nih.gov/pmc/articles/PMC4914586/) along with neuroplasticity (https://www.ncbi.nlm.nih.gov/pmc/articles/PMC6296269/) and angiogenesis (https://www.ncbi.nlm.nih.gov/pmc/articles/PMC5577549/) to meet the new demands on the neurons as they form new connections and modify old ones. It all happens all at once as a complex system, and the non-neuronal cell structures might still be doing much more to contribute to consciousness and memory beyond maintaining homeostasis. What we can take away, however, is that we have the full ability to influence this whole system through exercise, especially with our breath.

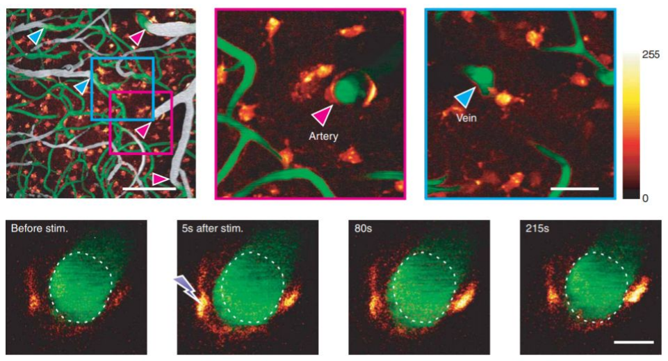
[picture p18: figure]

Astrocytes stimulated (orange) to induce arterial vasodilation (green). Source: Astrocyte-mediated control of cerebral blood flow (http://www.cns.nyu.edu/events/spf/SPF_papers/takano_etal_2006.pdf) - Takano et. al. (2006)

These different cellular phenomena in the brain demonstrate a clear and verifiable precedent for how breathing and increasing blood flow via exercise can have real structural and functional changes in many key areas of the brain, related to all kinds of mental processes and psychiatric issues. It shows how intense the cellular processes really are for just building the infrastructure that supports your biological neural network, and how it must adapt at every step of the way to keep up with your learning and living.

Breathing exercise specifically has several well-mapped and interesting relationships to mental processing via breathing’s specific coupling with many different important brain systems. This is likely due to its big role in keeping us alive, sensing, and communicating. It’s just like how all of the other functions we perform are now being found to have specific networks in our brain, and we can stimulate those networks to grow and reinforce by performing and practicing those functions along with practicing good health. This also offers a way to interact with and remediate many of the involuntary CBF changes cited in the studies at the beginning of this section and in countless others not highlighted. The brain is like a muscle in that sense, and must “fire together to wire together.” This exercise can also increase uptake of different types of learning and memorization as a priming method.

With this all in mind, what I suggest is simply that we have a very interesting and universal way to better understand and reinforce many systems in our brain. It offers the opportunity to reinforce our mind-body connection very pragmatically, and just with simple controlled breathing exercises. It’s nothing new, but I am attempting to link it with clinical evidence down to the cellular level so there is much less doubt about this reality and more dignity for its practitioners. However, with a clearer holistic model developed as more related physiological studies come out, we ought to be able to use this as a kind of old-school but valid deep brain stimulation. (https://www.ncbi.nlm.nih.gov/pmc/articles/PMC3969941/) We can likely learn to very specifically regulate activity in different parts of the brain associated with different mental processes - places otherwise out of reach - with the aid of different breathing techniques to see how functional, morphological, and psychological changes may occur in response. The point is to better understand how we may provide people more relief from mental illnesses and a chance to excel in themselves by more noninvasive, non-pharmacological means so that there are more options and more prevention (of which there are few). This can and should be done with the assistance of low cost monitoring technology like fNIRS for maintaining objectivity as well as introducing new ways to interact with ourselves directly or indirectly.

With regards to the self-interaction allowed by technology, not all of this is conscious and our body is able to interact with much more complex sensory information to inform itself than we may initially realize due to our limited top-down awareness. A great 2015 TED talk (https://www.ted.com/talks/david_eagleman_can_we_create_new_senses_for_humans?language=en) with David Eagleman highlights his contributions on measuring information throughput via vibrations on the skin (https://link.springer.com/article/10.1007/s00221-015-4346-1) (akin to how we read braille). His team found that within days a deaf person could learn to interpret vibrations on a vest, corresponding to audio inputs encoded in specific vibratory patterns, and could interpret spoken words very easily without lip reading. What we can extrapolate from this is that our bodies are processing and encoding much more information and are capable of internalizing all kinds of abstract models for language and self-regulation. This helps indicate that biofeedback - or adding some extra sensors to better indicate our physiological states - has real implications at both the conscious and unconscious levels. Taking this further, our bodies use all of the sensory input it can get to help regulate its internal processing and form new communication pathways to itself and the external world in tandem via reinforcement learning. We are like cybernetic octopuses disguised as apes or something.

Bringing this back down a peg, dozens of case studies over the past two and a half decades indicate repeatable, predictable responses to HEG biofeedback across hundreds of users either considered healthy or with different major symptom profiles like PTSD (https://www.csusb.edu/sites/default/files/upload/file/2016_Reiter%2C%20Andersen%2C%20Carlsson_Neurofeedback%20Treatment%20and%20PTSD_0.pdf) and ADHD. (https://pubmed.ncbi.nlm.nih.gov/29658934/) The next section contains a list of case studies (most of the ones I can find on the internet) and show positive results across the board. I did not have to cherry pick.

List of HEG Case Studies
Here is an informal list of links to many widely varied case studies across many institutions and describe many testable treatment protocols for using the HEG effectively:

Intentional Increase of Cerebral Blood Oxygenation Using Hemoencephalography (HEG): An Efficient Brain Exercise Therapy - Toomim et. al. https://www.tandfonline.com/doi/abs/10.1300/J184v08n03_02?src=recsys

Effects of HEG training at three prefrontal locations - Sherrill https://www.tandfonline.com/doi/abs/10.1300/J184v08n03_05?src=recsys

HEG Neurofeedback Mechanism of Action (ASD focused) - Shoshev https://www.researchgate.net/profile/Mitko_Shoshev/publication/323699457_Hemoencephalography_neurofeedback_-_mechanism_of_action/links/5ab8b34045851515f59f8fc9/Hemoencephalograp hy-neurofeedback-mechanism-of-action.pdf (https://www.researchgate.net/profile/Mitko_Shoshev/publication/323699457_Hemoencephalography_neurofeedback_-_mechanism_of_action/links/5ab8b34045851515f59f8fc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)

Clinical Usefulness of HEG - Serra Sala et. al
https://www.ncbi.nlm.nih.gov/pmc/articles/PMC4869785/

Passive Infrared HEG: 4 years and 100 migraines - Carmen https://www.tandfonline.com/doi/abs/10.1300/J184v08n03_03

HEG Case studies - Toomim and Carmen https://www.brainchanger.co/wp-content/uploads/2018/07/heg_case_studies.pdf

HEG A New Therapy for ADHD: Case Report - Mize https://www.tandfonline.com/doi/abs/10.1300/J184v08n03_06

Evaluation of PFC activation and emotional processing with HEG - Gallart https://www.tandfonline.com/doi/abs/10.1080/10874208.2012.705754

Passive Infrared HEG - Carmen https://www.eeginfo-neurofeedback.se/fileadmin/images/was_ist_neurofeedback/literatur/pIR_HEG_article_10_25_01.pdf (https://www.eeginfo-neurofeedback.se/fileadmin/images/was_ist_neurofeedback/literatur/pIR_HEG_article_10_25_01.pdf)

HEG for Dyslexia - Pecyna
https://link.springer.com/chapter/10.1007/978-94-007-6627-3_26

HEG for Schizophrenia vs Healthy participants - Gomes et. al. https://www.sciencedirect.com/science/article/abs/pii/S0920996417305200

HEG for Migraines without aura - Walker and Lyle http://www.neuroregulation.org/article/view/16213

HEG training for improving brain function with EEG comparisons - Bartosinski et. al. http://82.139.152.144/index.php/pjas/article/download/133/110

HEG training for children with and without ADHD - HEG and QEEG comparisons - Castro et. al. https://www.sciencedirect.com/science/article/abs/pii/S0924933814778095

HEG training with EEG data compared - Sherrill https://www.tandfonline.com/doi/abs/10.1300/J184v08n03_05

### 37 Migraine patients studied with EEG + HEG + Skin temperature - Stokes and Lappin

https://link.springer.com/article/10.1186/1744-9081-6-9

HEG Alpha
So where are we at right now? There are many emerging fNIRS technologies on the market of varying complexity and an even more variable cost, though it is dropping on average like all commercial technologies. I myself have produced a single sensor fNIRS HEG board, first as a cheap off-the-shelf kit and now a more competent and state of the art design using the MAX86141 with a modular and flexible breakout board style. It can be either a foldable fingertip pulse oximeter or fNIRS sensor. These are currently available at https://hegalpha.com as developer kits and come with a simple but functional headband to make it a wearable biofeedback device. The original kit was launched successfully on Crowd Supply and picked up by OpenBCI for their shop. We have sold hundreds without much budget for advertising or flashy designs due to its highly practical purpose.

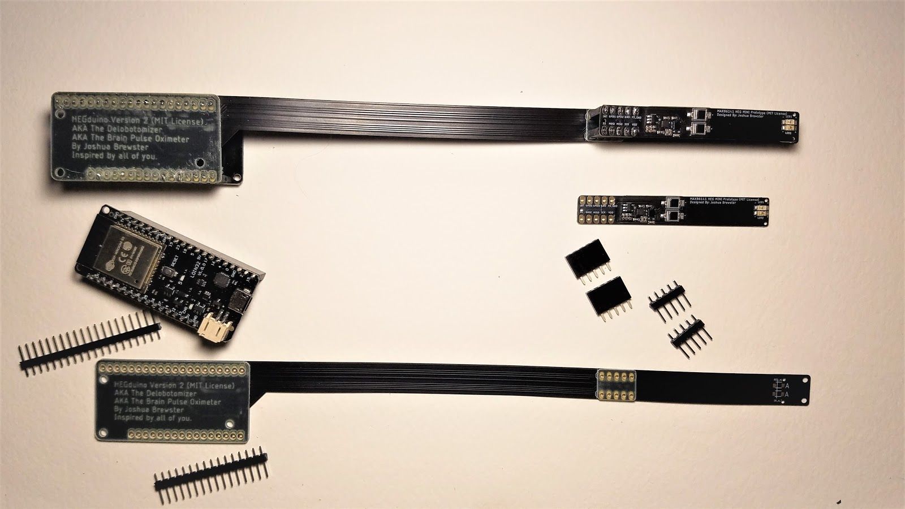
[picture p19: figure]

The Delobotomizer kit features an ESP32 to drive the MAX86141, enabling Bluetooth, WiFi, and Serial USB data transmission and lightweight onboard software via a web server to deliver a robust HTML5 interface. This was developed over the last year and a half with the help of Brain Trainer (from Georgia) and John Chibuk (BlueberryX in Toronto) at certain phases while I helped them prototype their own designs. My own version is available open source under the MIT license or as a purchasable developer kit to support my continuing public domain work.

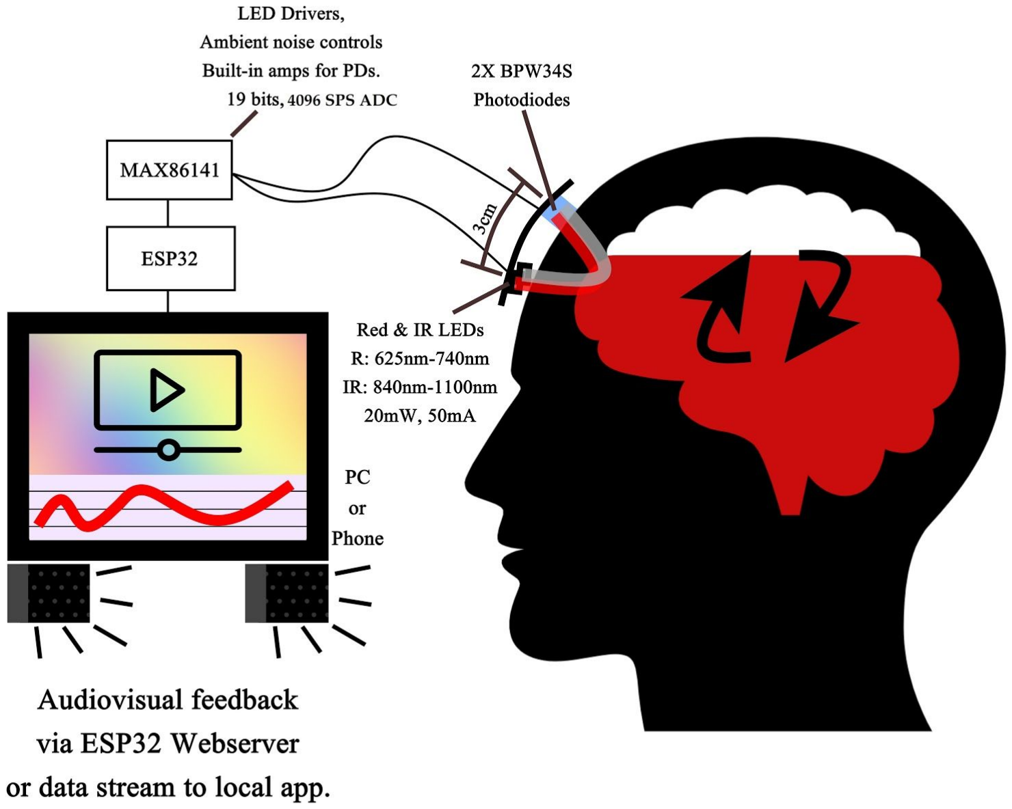
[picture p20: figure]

The MAX86141 is a dual channel 4096sps 19 bit ADC with built in amps and LED drivers to manage photodiodes and up to 6 LEDs. The MAX86141 also has its own automatic data buffering system and some nice hardware noise reduction algorithms to sweeten the deal, all for about $5 in a barely visible BGA package (see if you can spot it above). We used the highest sensitivity photodiodes we could find
- the BPW-34S and bright, fast-pulsing ~650nm and ~950nm LEDs, standard wavelengths for pulse oximetry using common SpO2 algorithms. (https://www.maximintegrated.com/en/design/technical-documents/app-notes/6/6845.html)

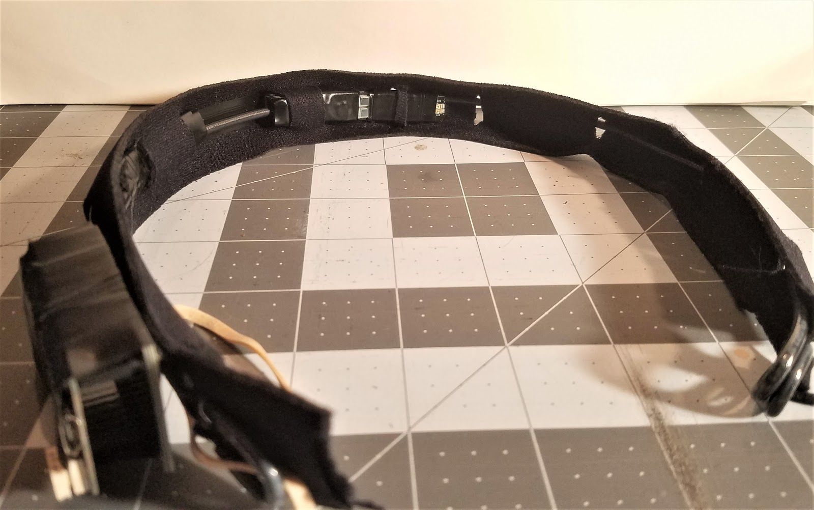
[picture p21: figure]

HEGduino: The Delobotomizer, a homemade wearable dev kit.

Users wear this device on their heads with a simple headset and interact with our streamlined cross-platform javascript software. At the time of writing this exists as either the on-board HTML5 app or a Chrome extension which enables USB or Bluetooth connectivity via virtual COM port.

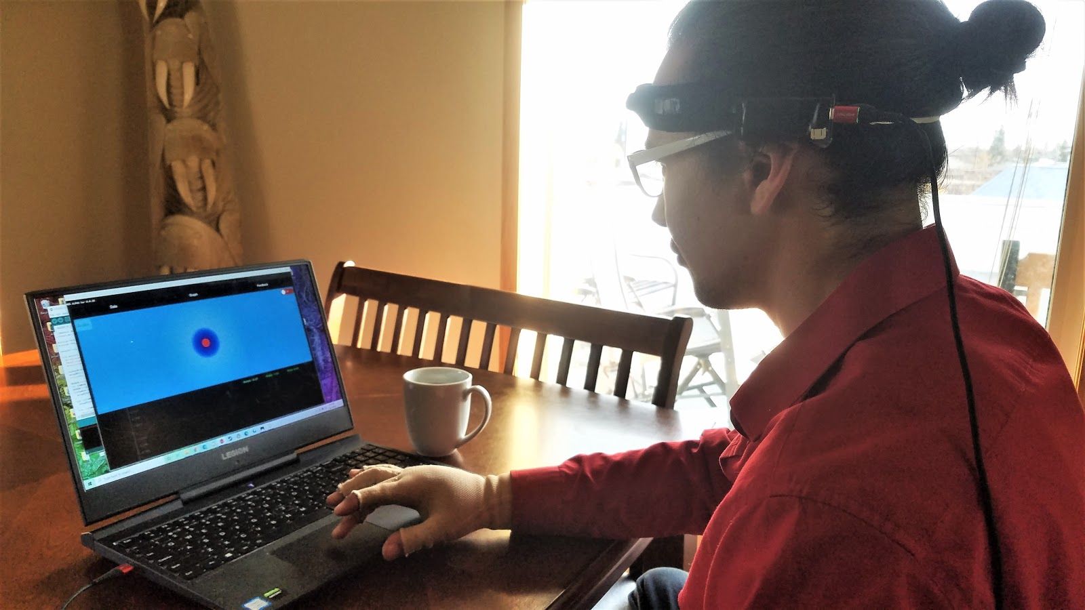
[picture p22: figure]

A user interacting with the software. His brain blood flow creates changes to the different visuals on-screen to help with self-guided biofeedback. Guided exercises and more sophisticated conditioning tools can be developed, while the current visualizations are all passive - which are more ideal for casual sessions.

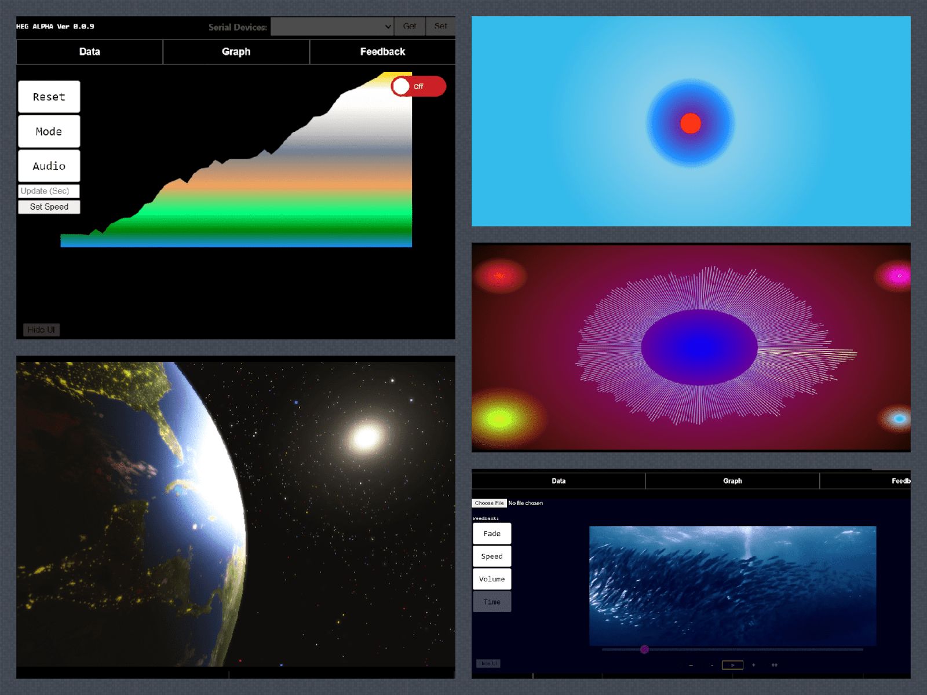
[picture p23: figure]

The interface contains different 2D, 3D, audio, and video feedback options. These are coded entirely modularly via classes with a homogenized format so the API is easy to learn and more features are fairly trivial to plug in or develop on top of. With vanilla HTML5/CSS/JS as the base, it can also be plugged into phone apps or websites to offer robust cross-platform accessibility or remote play. This is now being demonstrated with a Progressive Web App implementation which will provide cross platform access and will be downloadable from a single link on the web.

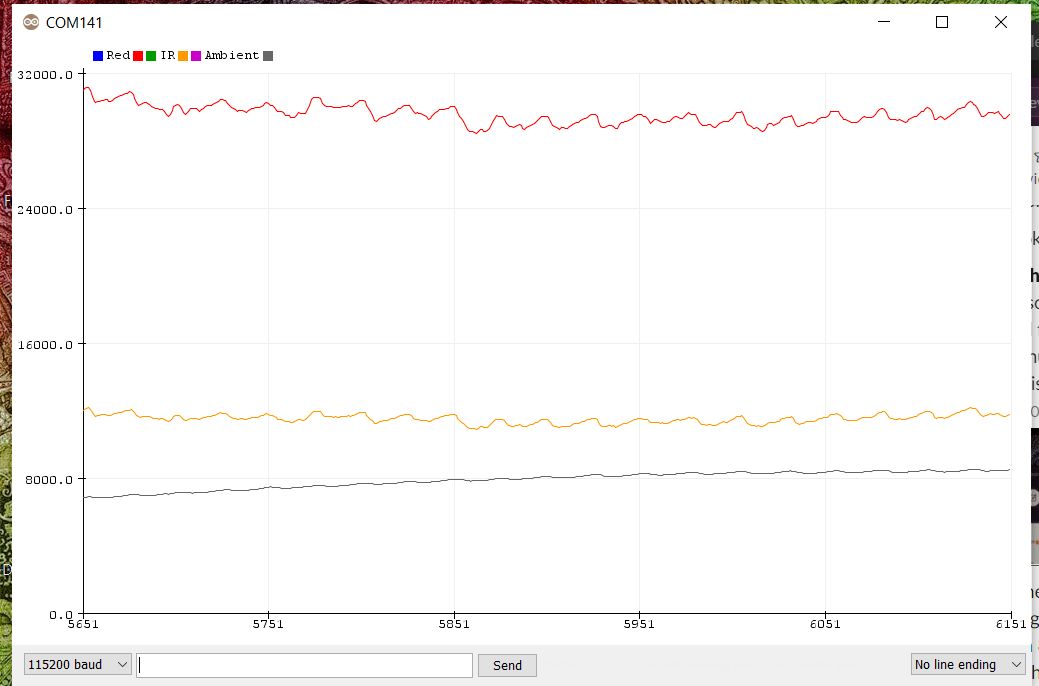
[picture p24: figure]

Data off the forehead with the Delobotomizer (I just like saying it) at 3cm spacing and 29.4us 124mA LED pulses, averaging 32 samples for each pulse at 2048sps. This was not a great controlled test but this was shoving as hard as I could into my scalp to minimize scalp signal. You can see pulse amplitudes even in the ambient light, and even the blood pressure waveforms in the Red and Infrared. While you can see that the Red signal is double the IR, at times it is the other way around depending on location and your physical state. There are rapid, dramatic changes visible even with a 1 sensor signal. This is all done in Arduino since it’s a piece of cake to work with.

The goal with the software was to make the beginnings of an open and relevantly formatted BCI software API and simple game engine (including easy and lightweight plugins like ThreeJS). Each class contains default instantiations of the contained visual features so it’s easier to build a UI and then modify it with CSS. Everything is handled with document fragments for creating highly performant webapps. Web and game engines have also improved dramatically with many standard
communication protocols now on hand to interact with hardware streams, and the ESP32 on the HEG allows a wide variety of ways to connect to different local or remote interfaces. The more generic and reusable we make this API, the easier it is to build a professional feature set in less time on any platform (or all platforms). My goal is to be able to offer comparable software to the professional ones by this method, for free, and make it a robust and performant BCI platform as well as a launchpad for future, better iterations. This is all in a format that is not likely to become obsolete in the near future -rather even more feature-rich with Web 3.0 and the recent addition of great GPU tools like compute shading.

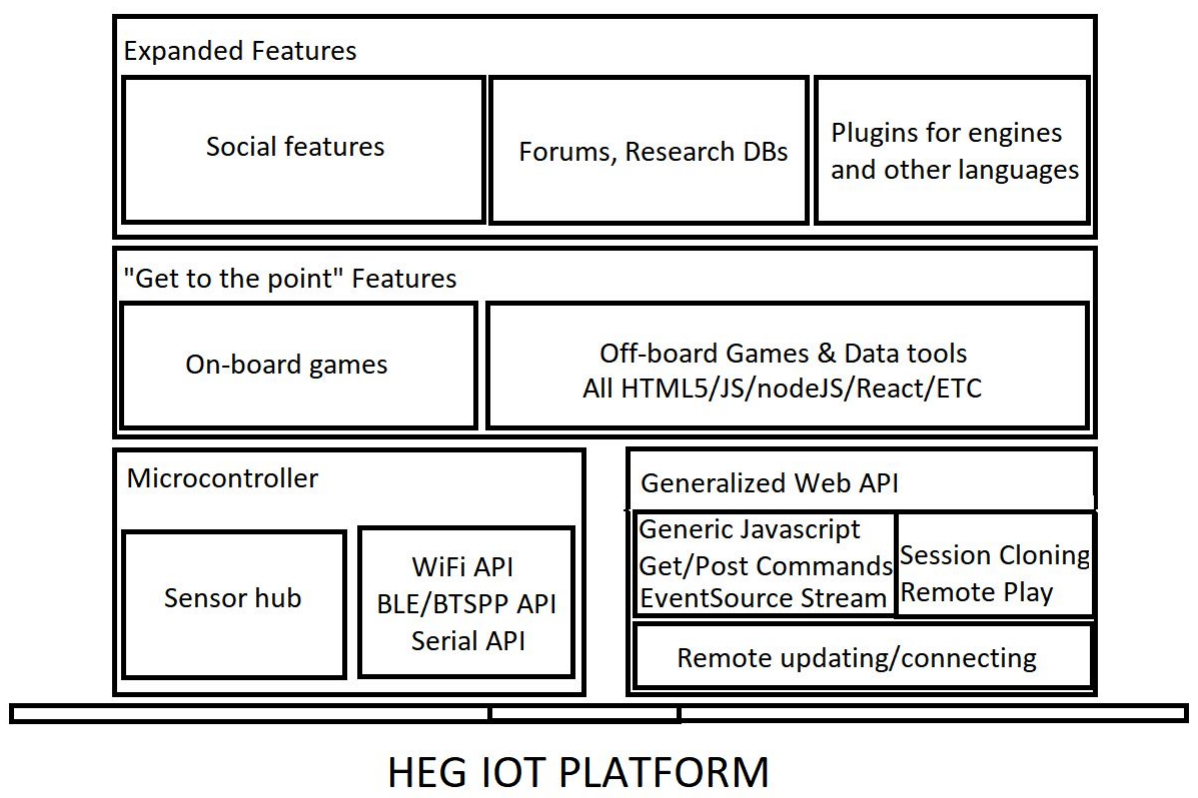
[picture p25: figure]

Here’s a rough idea of the modular software stack. It’s like a RESTful API so nothing gets wasted on the front or backend plus it prioritizes better information throughput and cleaner coding. The idea is to eventually integrate this all into a hosted web server to provide an interesting (but optional) online front end for general home BCI just to improve accessibility and make more use of the online connectivity potential between clients. A native phone application is also planned. You can see demos here: https://hegalomania.netlify.app and here: https://heg-alpha.netlify.app where one is a React port of the interface.

We are informally partnered with the FreeEEG32 project (https://www.crowdsupply.com/neuroidss/freeeeg32) and intend to lump EEG features into our API, and we are developing our own <$50 flexible DOT sensor set (MIT license) (https://github.com/moothyknight/DIY_DOT) to plug into the <$200 FreeEEG32 board (AGPL license). This DOT set mimics the visual cortex fNIRS array back in the fNIRS overview. With the FreeEEG32 as the A/D converter and extra boards tied together as LED drivers for the 24 LED pairs on the device this will be the lowest cost and most enthusiast-friendly DOT headset to date, and the goal is to work up to repeating the image reconstruction study also cited in the fNIRS overview and see if we can begin to parse what our visual cortex is seeing.

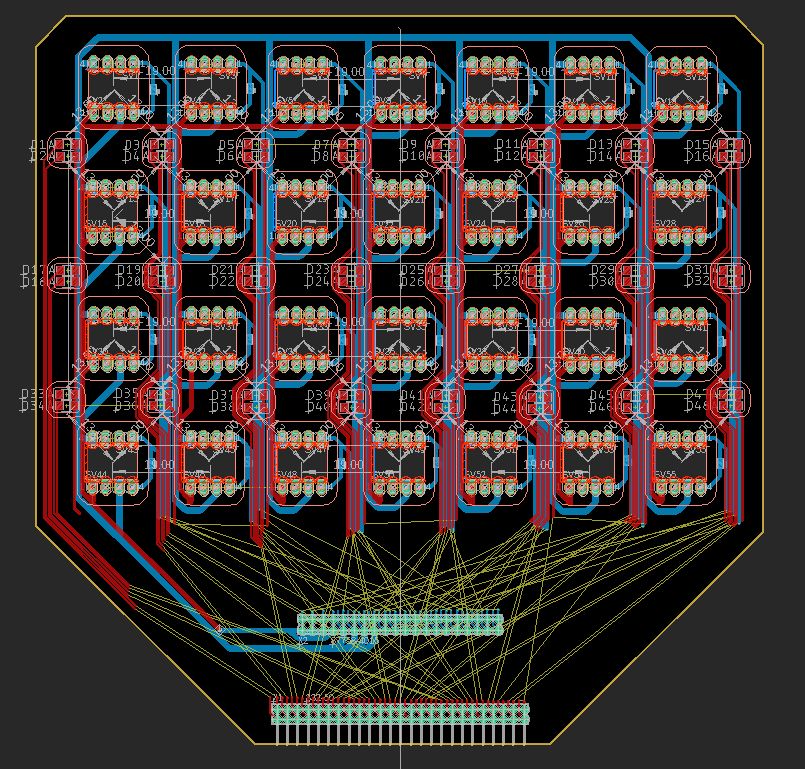
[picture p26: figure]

We are trying to work our way through this weird and wonderful realm of light based sensing and brains. We are developing low cost biofeedback tools and graduating ourselves to imaging, without leaving any stone unturned along the way so that we are continually putting out practical tools for common use and articulating important ideas as best we can. We’re exploring the associated mathematics and doing as much ourselves as possible so we can safely open source it for free and low cost use, as enabling more and more inquiry and collaboration for this fascinating space is a most important goal.

Other interesting open source fNIRS projects to check out:
ninjaNIRS: https://openfnirs.org
OpenNIRS: https://opennirs.org

This will hopefully carry over into a wider coordinated effort with a lot more people involved as we explore new frontiers. Get in touch and let me know your ideas/efforts if you want to collaborate at https://hegalpha.com.

Citations from Hyperlinks
This section is to highlight all of the studies and articles in the embedded links throughout the paper (click on them if you are viewing on a computer). Check all of them out, there are more than 60 links throughout this article, and you haven’t really learned anything if you haven’t looked further beyond my paper as they contain tons of detailed information and images.

Toomim, Marsh. “Biofeedback of human central nervous system activity using radiation detection” USPTO. 1996.
https://patents.google.com/patent/US5995857A/en

Carp et. al. “Diffuse correlation spectroscopy measurements of blood flow using 1064nm light” Journal of Biomedical Optics. 2020. https://www.spiedigitallibrary.org/journals/journal-of-biomedical-optics/volume-25/issue-09/097003/Diffuse-correlation-spectroscopy-measurements-of-blood-flow-using-1064nm-light/10.1117/1.JBO.25.9.097003.full?fbclid=IwAR02-l_q-xCykuuqUjc_RWJfQE7ESOEIRK0G9mqZSWaGiFhfwu1QNV42vjQ&SSO=1 (https://www.spiedigitallibrary.org/journals/journal-of-biomedical-optics/volume-25/issue-09/097003/Diffuse-correlation-spectroscopy-measurements-of-blood-flow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)

Zeff et. al. “Retinotopic mapping of adult human visual cortex with high-density diffuse optical tomography” National Academy of Sciences. 2007
https://www.pnas.org/content/104/29/12169

Anwar. “Scientists use brain imaging to reveal the movies in our mind” Berkeley News. 2011. https://news.berkeley.edu/2011/09/22/brain-movies/

Shen, Horikawa, Majima, Kamitani. “Deep image reconstruction from human brain activity” PLOS Computational Biology. 2019. https://journals.plos.org/ploscompbiol/article?id=10.1371/journal.pcbi.1006633

Wang et. al. “CNN Explainer” Github. 2020.
https://github.com/poloclub/cnn-explainer

Wang et. al. “CNN Explainer: Learning Convolutional Neural Networks with Interactive Visualization” IEEE VIS 2020. (2020)
https://arxiv.org/abs/2004.15004

O’Sullivan, Hoffman, Paulson. “Reality is Not As It Seems” New York Academy of Sciences. 2019. https://www.youtube.com/watch?v=3MvGGjcTEpQ

Gratton, Fabiani. “Chapter 15, Fast Optical Signals: Principles, Methods, and Experimental Results” In Vivo Optical Imaging of Brain Function. 2009. https://www.ncbi.nlm.nih.gov/books/NBK20223/#:~:text=Fast%20optical%20signals%20are%20rec ently,through%20the%20intact%20human%20brain. (https://www.ncbi.nlm.nih.gov/books/NBK20223/)

Espigares et al. “Assessment of natural enamel lesions with optical coherence tomography in comparison with microfocus x-ray computed tomography” Journal of Medical Imaging. 2015. https://pubmed.ncbi.nlm.nih.gov/26158079/

Su et. al. “Imaging the anterior eye with dynamic-focus swept-source optical coherence tomography” Journal of Biomedical Optics. 2015
https://pubmed.ncbi.nlm.nih.gov/26662065/

“Wim Hof” Wikipedia. 2020.
https://en.wikipedia.org/wiki/Wim_Hof

Herrero, Khuvis, Yeagle, Cerf, Mehta. “Breathing above the brain stem: volitional control and attentional modulation in humans.” Journal of Neurophysiology. 2018. https://journals.physiology.org/doi/full/10.1152/jn.00551.2017

Jhang et. al. “Anterior cingulate cortex and its input to the basolateral amygdala control innate fear response.” Nature Communications. 2018. https://www.nature.com/articles/s41467-018-05090-y

Moberly et. al. “Olfactory inputs modulate respiration-related rhythmic activity in teh prefrontal cortex and freezing behavior” Nature Communications. 2018. https://www.nature.com/articles/s41467-018-03988-1

Riachle, Gusnard. “Appraising the brain’s energy budget” National Academy of Sciences. 2002. https://www.ncbi.nlm.nih.gov/pmc/articles/PMC124895/

Kuzawa, Blair. “A hypothesis linking the energy demand of the brain to obesity risk” National Academy of Sciences. 2019.
https://www.pnas.org/content/116/27/13266

Tata, Ruhrberg, Fantin. “Vascularisation of the central nervous system” Mechanisms of Development. 2015.
https://www.ncbi.nlm.nih.gov/pmc/articles/PMC4678116/

Kim, Park, Choi. “The Role of Astrocytes in the Central Nervous System Focused on BK Channel and Heme Oxygenase Metabolites: A Review” Antioxidants. 2019. https://www.ncbi.nlm.nih.gov/pmc/articles/PMC6562853/

Marina et. al. “Astrocytes monitor cerebral perfusion and control systemic circulation to maintain brain blood flow” Nature Communications. 2020. https://www.nature.com/articles/s41467-019-13956-y

Mirgain et. al. “Whole Health: Change the Conversation. The Power of Breath: Diaphragmatic Breathing Clinical Tool” Veteran’s Health Affairs. 2016 http://projects.hsl.wisc.edu/SERVICE/modules/12/M12_CT_ThePowerOfBreathDiaphragmaticBr eathing.pdf (http://projects.hsl.wisc.edu/SERVICE/modules/12/M12_CT_ThePowerOfBreathDiaphragmaticBreathing.pdf)

Peteri, Niukkanen, Castren. “Astrocytes in Neuropathologies Affecting the Frontal Cortex” Frontiers in Cellular Neuroscience. 2019. https://www.ncbi.nlm.nih.gov/pmc/articles/PMC6379461/#:~:text=Astrocytes%20comprise%20of %20a%20heterogeneous,region%20especially%20susceptible%20to%20damage. (https://www.ncbi.nlm.nih.gov/pmc/articles/PMC6379461/)

Tatsumi et. al. “Voluntary Exercise Induces Astrocytic Structural Plasticity in the Globus Pallidus” Frontiers in Cellular Neuroscience. 2016.
https://www.ncbi.nlm.nih.gov/pmc/articles/PMC4914586/

Lin, Tsai, Kuo. “Physical Exercise Enhances Neuroplasticity and Delays Alzheimer’s Disease” Journal of Brain Plasticity. 2018
https://www.ncbi.nlm.nih.gov/pmc/articles/PMC6296269/

Ballard. “Exercise makes your brain bigger: skeletal muscle VEGF and hippocampal neurogenesis” Journal of Physiology. 2017.
https://www.ncbi.nlm.nih.gov/pmc/articles/PMC5577549/

Takano et. al. “Astrocyte-mediated control of cerebral blood flow” Nature Neuroscience. 2006. http://www.cns.nyu.edu/events/spf/SPF_papers/takano_etal_2006.pdf

Fenoy, Goetz, Chabardes, Xia. “Deep Brain Stimulation: Are Astrocytes a Key Driver Behind the Scene?” CNS Neuroscience & Therapeutics. 2014. https://www.ncbi.nlm.nih.gov/pmc/articles/PMC3969941/

Eagleman. “Can we create new senses for humans?” TED. 2015. https://www.ted.com/talks/david_eagleman_can_we_create_new_senses_for_humans?language=en

Novich, Eagleman. “Using space and time to encode vibrotactile information: toward an estimate of the skin’s achievable throughput” Experimental Brain Research. 2015. https://link.springer.com/article/10.1007/s00221-015-4346-1

Reiter, Anderson, Carlsson. “Neurofeedback Treatment and Posttraumatic Stress Disorder” The Journal of Nervous and Mental Disease. 2016. https://www.csusb.edu/sites/default/files/upload/file/2016_Reiter%2C%20Andersen%2C%20Carlsson_Neurofeedback%20Treatment%20and%20PTSD_0.pdf (https://www.csusb.edu/sites/default/files/upload/file/2016_Reiter%2C%20Andersen%2C%20Carlsson_Neurofeedback%20Treatment%20and%20PTSD_0.pdf)

Areces et. al. “Using Brain Activation (nir-HEG/Q-EEG) and Execution Measures (CPTs) in a
ADHD Assessment Protocol” Journal of Visualized Experiments. 2018. https://pubmed.ncbi.nlm.nih.gov/29658934/

“Guidelines for SpO2 using the MAXIM MAX32664 Sensor Hub” MAXIM Integrated. 2019 https://www.maximintegrated.com/en/design/technical-documents/app-notes/6/6845.html

Sukhoruchkin, Brewster, Markus. “FreeEEG32” Crowd Supply. 2020 https://www.crowdsupply.com/neuroidss/freeeeg32

Brewster, “DIY Diffuse Optical Tomography” Github. 2020. https://github.com/moothyknight/DIY_DOT

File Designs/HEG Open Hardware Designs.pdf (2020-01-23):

HEG Open Hardware Designs

MIT License
Copyright 2019, Joshua Brewster

Permission is hereby granted, free of charge, to any person obtaining a copy of this hardware, software, and associated documentation files (the "Product"), to deal in the Product without restriction, including without limitation the rights to use, copy, modify, merge, publish, distribute, sublicense, and/or sell copies of the Product, and to permit persons to whom the Product is furnished to do so, subject to the following conditions:

The above copyright notice and this permission notice shall be included in all copies or substantial portions of the Product.

THE PRODUCT IS PROVIDED "AS IS", WITHOUT WARRANTY OF ANY KIND, EXPRESS OR IMPLIED, INCLUDING BUT NOT LIMITED TO THE WARRANTIES OF MERCHANTABILITY, FITNESS FOR A PARTICULAR PURPOSE AND NONINFRINGEMENT. IN NO EVENT SHALL THE AUTHORS OR COPYRIGHT HOLDERS BE LIABLE FOR ANY CLAIM, DAMAGES OR OTHER LIABILITY, WHETHER IN AN ACTION OF CONTRACT, TORT OR OTHERWISE, ARISING FROM, OUT OF OR IN CONNECTION WITH THE PRODUCT OR THE USE OR OTHER DEALINGS IN THE PRODUCT.

HEGduino kit

This design is based off the original, now-expired HEG patent 5995857 by Hershel Toomim and Bob Marsh. The original sensor design is simply an OPT101 spaced at 3cm from 2 50mA LEDs
- one in the Red spectrum and one in the Infrared spectrum. The Red LED is set at 650nm and the Infrared LED is set at either 850nm or 950nm. 850nm provides more linear scaling for blood flow ratio, while 950nm is the industry standard for pulse oximetry.

Our microcontroller of choice is the Espressif ESP32 using Arduino libraries, available for ~5 dollars on average, with our firmware available for free under the MIT license at https://github.com/moothyknight/HEG_ESP32. We also originally accomplished it with an Arduino Nano v3 which we purchased for 1 dollar apiece plus shipping. We are utilizing the ESP32 for its IoT capabilities which allows full interaction via a local webserver on the device itself. It also can connect online for remote data collection abilities or use bluetooth as well as traditional serial methods. None of our work is original on this in the sense that we used wholly open source libraries to develop the software solution, aside from our own simple method for driving the LEDs and timing the readings.

Continue below for multiple designs.

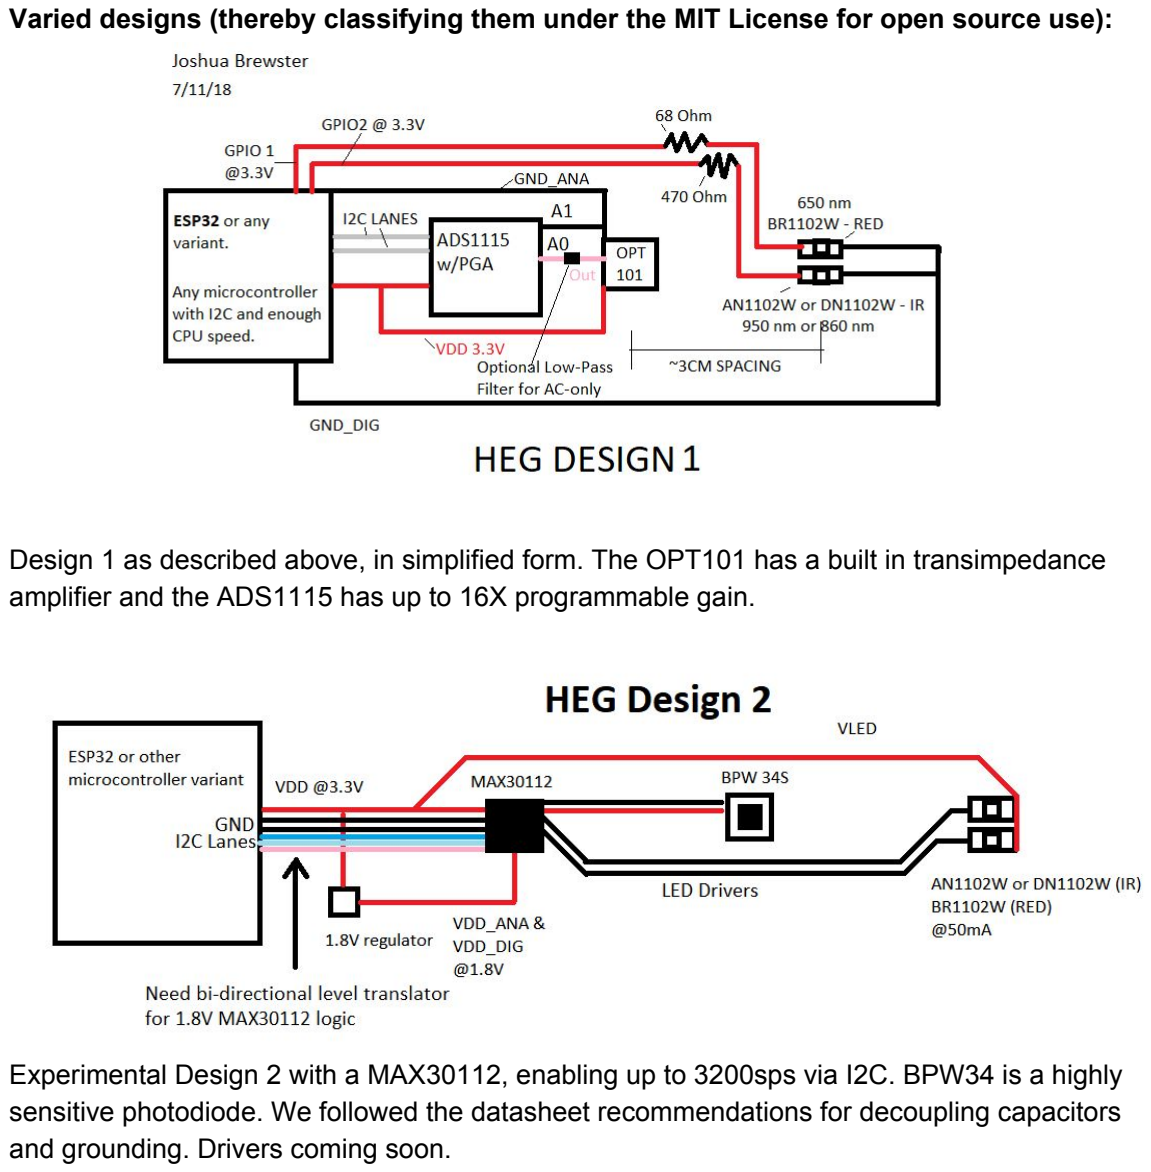
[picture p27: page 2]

Varied designs (thereby classifying them under the MIT License for open source use):

Design 1 as described above, in simplified form. The OPT101 has a built in transimpedance amplifier and the ADS1115 has up to 16X programmable gain.

Experimental Design 2 with a MAX30112, enabling up to 3200sps via I2C. BPW34 is a highly sensitive photodiode. We followed the datasheet recommendations for decoupling capacitors and grounding. Drivers coming soon.

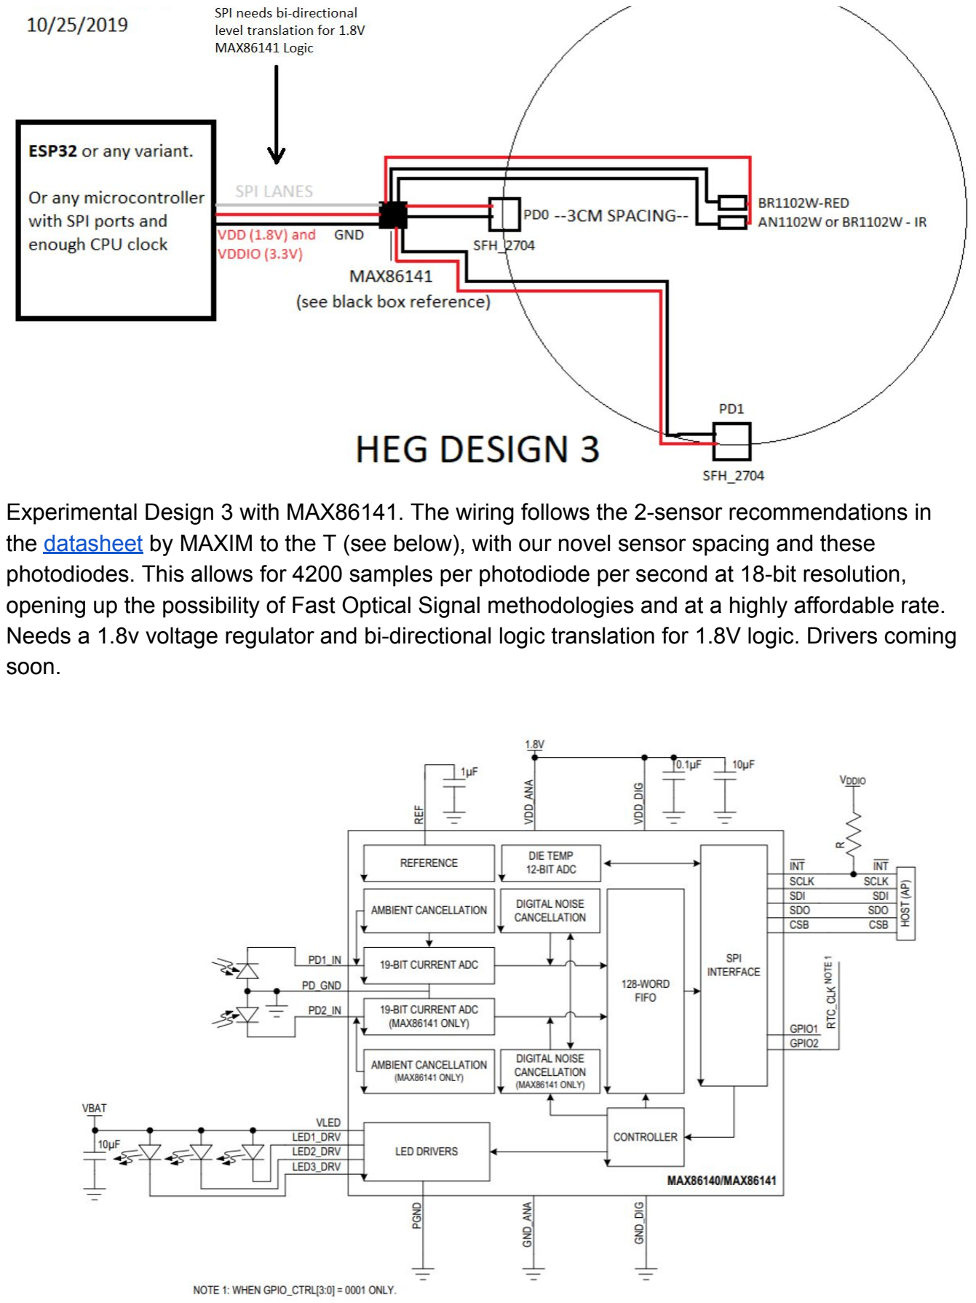
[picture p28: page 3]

Experimental Design 3 with MAX86141. The wiring follows the 2-sensor recommendations in the datasheet (https://datasheets.maximintegrated.com/en/ds/MAX86140-MAX86141.pdf) by MAXIM to the T (see below), with our novel sensor spacing and these photodiodes. This allows for 4200 samples per photodiode per second at 18-bit resolution, opening up the possibility of Fast Optical Signal methodologies and at a highly affordable rate. Needs a 1.8v voltage regulator and bi-directional logic translation for 1.8V logic. Drivers coming soon.

Above is the reference sheet provided by MAXIM, we followed this exactly and included ground planes wherever possible for improved isolation and decoupling. The MAX86141 should be as close to the photodiode site as possible.

As you can see, it’s fairly easy to design these things, the key is finding the best and most affordable parts - which improve year to year. These are a solid foundation to begin from. And yes, I used Paint for these diagrams… but I recommend EAGLE or KiCAD for some of the better PCB design tools.

More design notes on next page...

More detailed view of Design 1, minus the optional GND_ANA to A1 on the ADS1115 (for differential output):

Design notes:


There are several key design ideas to keep in mind when developing the sensor.

1st: The sensor distance tells you roughly how deep of a signal you are reading. You are measuring an arc that is a slice of a field generated by each LED flash, the distance of that arc depending on the distance of the sensor from the photodiodes. The distance limit is based on safe LED intensity as well as tissue absorption, enabling up to about 5cm deep of penetration according to Event Related Optical Signal tests in nIR light penetration. Toomim and Marsh recommend 2.2 to 3.5cm with the LEDs used in these designs according to patent 5995857.

2nd: The analog and digital components need separate ground lines/planes from the sensor to prevent feedback from the LED voltages. The analog output should also be shielded with copper planes to minimize noise.

3rd: The closer you can get the ADC to the signal output the better, movement can generate static and add noise if there is more wire between the ADC and sensor.

4th: You don’t need more than 100 samples per second and 16 bits for good signal fidelity. We demonstrated this with a minimum-bar ADS1115, which includes PGA and differential modes to get pretty decent signal. We also recommend the MCP3424, an 18-bit, 240sps sigma-delta ADC which is more than enough for pulse oximetry, and simultaneous sensor data. These are both available as arduino kit-styled components.

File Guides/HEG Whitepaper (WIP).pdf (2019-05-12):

Open Source HEG Whitepaper The how’s, what’s, and why’s. Joshua Brewster

Abstract:

Hemoencephalography utilizes reflective red-infrared pulse oximetry to read and help gain control of blood-oxygen levels in brain regions or other parts of the body. The primary open source HEG model is built with widely used hardware and software solutions with the ESP-32, generic sensors and digital converters, and the Arduino IDE. This serves as a maximally affordable, maximally accessible, and maximally iterable foundation for what is to be seen as a much larger scientific and cultural endeavor. Let this project serve as an archetype of more projects like it, where this whitepaper will establish the desired results of the open source platform and the ethos underlying this attempt. Emphasis is placed on community, creativity, and collaboration.

Contents:

Preamble
Open Source Hemoencephalography Theory
The “Archetypal HEG”
Tech Specs
Code
Test Results
Ideal Future Directions
Potential Markets
Conclusion
Citations/Further Reading


Preamble:

Open source serves as an important pillar for most major successful commercial hardware and software businesses (e.g. Google, Facebook, Amazon, Android phone manufacturers, etc.), from the original academic research behind the electrical engineering and data structures, to many if not most of the programming APIs these commercialized technologies utilize. This process is driven by hundreds of mostly-anonymous contributors toiling away on their own use-cases, forking libraries and pushing updates as needed and generally in their spare time. Now people get hired specifically to improve open source libraries for companies that rely on them under the hood, which gets propagated to everyone else worldwide under open source licenses like the GPL license. Less strict open source licenses like LGPL, MIT (our license of choice for this project), or even the Unlicense allow monetization and privatization of offshoots of these libraries.

Every programming language in mainstream use is open source. Even Iphones are made of mostly open source, public university-developed technology. As transistor and miniaturization costs continue to plummet in the manufacturing world, it’s now viable to even build your own Android phone. The Maker movement, centered around 3D printing and STEM education, relies entirely on open sourced patents in what was once a market restricted by only one company. Facebook company coders spend much of their resources on building powerful open source libraries, which fuels the adoption rate of their commercial products that are already integrated with said libraries. Open source tech is precisely the opposite of intellectual property, it’s everyone’s, while it leaves the door open for profit.

What this all reveals is one of the most important structures in the advancement of computer and human infrastructure. That’s the open, honest collaboration between people just trying to get things done and make common utilities that much more efficient and smooth both for creators/engineers and consumers. This naturally lends to commercializing niches that require the specialized, time-consuming work to justify monetization - and help engineers and creators survive. This then informs the general functionalities that need to be further developed in the open source realm, which makes everybody’s lives easier.

Many incredible commercial software platforms have been made free and open source because of this collaborative streamlining that happens when you have thousands of programmers investing their time for their own needs. Unreal Engine and Unity Engine, Sony’s animation software, Google’s data science APIs, etc. In spite of the millions of dollars required to develop these platforms, their progenitor companies were able to open them up for everybody to create more commercial grade products of their own. It was the information and resource asymmetry combined with their expert systems that let these groups produce these tools first, not any necessary specialness or exclusivity of the ideas which have become important for everyone like other kinds of infrastructure. This is causing massive gains in their own long term profits, especially as other creators begin to call these platforms home for their always up-to-date standards - made possible by the hundreds of additional collaborators in their own spaces who are all moving the computer field forward.

Above business and profit, open source provides endless educational material. The initial run of open source, arduino-based HEGs will be kits made in this vein, as it will maximize learning potential for creators and modders at any age. This is an important first step as the kits scale from a single unit being available and in play up to thousands without much difficulty and excellent cost scaling, and guarantees information proliferation that is most necessary for emerging tech or any fields of study and application in general. Good, ethical innovation is always the result of collective effort on several levels, even if it is not always immediately obvious. We believe this identifies the first and most important base that needs to be served, as these collective infrastructure-bound technologies truly belong to everyone.

Open Source Hemoencephalography (HEG):

This HEG open source project is an attempt at creating a fundamental platform for others to build their own work on, and through the spirit of community roll whatever improvements they make to the general model into the open source resource pool. As the HEG itself is built entirely from maximally affordable open source tools, this leverages well-curated and deep learning resources with minimized risk to experimenters. There are ample opportunities to profit on top of this platform too, from building enhanced hardware and software packages for sale to running practices or doing research. A fully realized open source toolset will have a commercial quality on desktop and mobile and more right out of the box, so as to set a high quality standard for what content we believe should be free - which is most of it. The learning content will be academically up-to-date and to-standard with peer-reviewed sources, to set an intellectual and ethical bar that should only be surpassed by further contributions.

Theory:


Hemoencephalography is a very cheap, efficient method to gain deeper insight into the health of the outer regions of the brain - the neocortex and white matter circuits. [1] It does this by measuring blood perfusion and metabolic activity through the skull in whatever area targeted by the Red/Infrared sensor, and is very similar to basic pulse oximetry. With readings, users can measure [2] and gain control of their own brain blood flow and metabolic activity in targeted regions, to do what have been coined “brain push-ups,” or exercises meant to improve the quality of blood flow in the target area of the neocortex, thus improving associated behaviors and functions. [3,4] It takes 5 minutes in a single session to gain control, unlike other methods which take far longer with less reliability. This was originally developed and patented in the 90's to treat ADD as a purified, non-invasive, and safe alternative to generally less reliable and more expensive EEG, SPECT, MRI, etc. biofeedback methods [5] of measuring brain activity and giving useful physical information back to the user.


Left: Light Absorbance of Hb vs HbO2. | Right: Dense capillary networks cover the brain
<1https://somepomed.org/articulos/contents/mobipreview.htm?13/55/14197> <http://www.sbirc.ed.ac.uk/cyril/MEEG4.html>

The neocortex is a layer 3-6mm thick that wraps around the outer part of your brain. It makes up about 76% of the brain's volume, uses about 80% of the blood and nutrient supply to the brain (30%-40% of the body's overall energy), and contains the most complex and mysterious natural circuitry we know of. It is unique to mammals, and humans have one of the largest brains relative to body size. [6]

The neocortex stores memories from all the senses, synthesizes language, makes up the frontal lobe that makes empathy and socialization possible, and even contains spatial maps of our physical world – as discovered in the winning experiment for the 2014 Nobel Prize in Medicine. It is broken up into many unique areas, from the empathy, logic, and language centers in the front and sides to the visual, auditory, and other sensory and movement processors toward the back. There can be a lot of crossover and overlap in the functions of these areas, something we owe our mental adaptability to as humans. In a similar vein, some symptoms are universal to mental health issues, like Hypofrontality, where the majority of the blood leaves our frontal lobe as part of our physical stress response, and can be mitigated with therapy. [7]


Simple HEG LIFE game by Brain Trainer

Knowing these facts, in tandem with current research on abnormal psychology like ADD, Depression (incl. Bipolar), Schizophrenia, PTSD, Dementia, and migraines to name a few... and in observation of emerging fields like Network Neuroscience and Behavioral Economics, it can be said with certainty that the general health of this neocortex - a dominant physiological feature that sets us apart from other animals – is an essential and often overlooked question when addressing human needs. It needs care, exercise, and stimulation like other parts of the body, and in more complex ways like the problems it developed to handle.


Adult vs toddler neocortex grey matter stains in various lobes. <https://www.researchgate.net/figure/Drawing-of-neocortical-layers-from-Ramon-y-Cajal-1911-Left-Nissl-staining-of-the-adult_fig3_2 81183803> (https://www.researchgate.net/figure/Drawing-of-neocortical-layers-from-Ramon-y-Cajal-1911-Left-Nissl-staining-of-the-adult_fig3_281183803)

HEG biofeedback is complementary to what most psychiatry and psychological treatments offer. It is cheap, safe, and easy enough to use to make it readily available to a much wider market than as purely a treatment tool – but also as a way to learn about and improve ourselves in general, especially when we have a very uninformed general population. We are at all-time high rates of mental illness and dependence in the United States, also 300 million people diagnosed with depression globally – recognized by the World Health Organization as one of the main contributors to disability and lost economic opportunity. [8]


SPECT Image of a former drug abuser’s brain pre- and post-HEG treatment. <http://smtp.biocompresearch.org/biofeedback-institute-stories.html>

The “Archetypal HEG”:

We are still working out minor details on the schematics for the final version, thus this whitepaper is subject to updates. However, full board files and schematics will be provided at the right time so as to make the open source HEG kits fully transparent and duplicable. There is immediate incentive to manufacture HEGs as they are not widely known or proliferated, while the information is mostly new and compelling (yet tied to long-standing health and wisdom traditions) - with everyone as a potential target user. Since we planned ahead, we will have sales of our archetypal “HEGduino” kit right as we are rolling out the open source launch. This grants us strategic advantage in that we should be able to stay ahead of the game as competitors begin to appear, while we have a fully realized product already under our belts. People tend to want to support the source, too, both because they simply want to be supportive or because of the authority that source contributors are granted for doing most of the work.

What is the archetype? This is the model to be the progenitor of further models. We designed a kit because it minimizes our manufacturing costs, the costs to buyers, and the risk of device failure when tinkering. We can incentivize engineers with free kits, free replacements, and co-collaborator name features (which look great on resumes). The circuitry itself is bare minimal, lacking several common features of other pulse oximeters, while still permitting the same amount of interactivity for biofeedback. The code is written in plain language with free programming tools. These were conscious choices for better cost scaling as well as demystifying the tech to tinkerers through the reduced complexity.


HEGduino kits. Features a flex board with stiffener, easy mounting of generic arduino components, and printed instructions on the boards.

Test Setup and Tech Specs:

Test Setup:

Recreating patent 5995857 specifications:


The original HEG sensor circuit is simply an LED flash timer and a buffer (the circuit on the right in the first image). The right image is the oscilloscope output result when placing the sensor on the forehead. You can see the signal is quite strong, within the mV range even with these low intensity LEDs. The noise is due to poor wiring and filtering. The higher amplitude square wave is the infrared pulse, the lower one is the red pulse. For comparison, the left image shows the results of the sensor under fluorescent light.

Sensor:
1x OPT101P Monolithic Photodiode
1x HAN1102W IR LED - 950nm*
1x BR1102W RED LED - 650nm

* DN1102W 850nm @ 20mA recommended by Biocomp


Arduino Setups:

BT/Wifi-capable microcontroller:
ESP32 dev board with arduino driver, we used Adafruit Huzzah32 and the Wemos Lolin32 series:

USB-only microcontroller:
Arduino Nano v3 (ATmega328p-based) will suffice:

The sensor specifications follow the original patent 5995857 [1]. The lights are 50mA 950nm IR and 650nm Red LEDs, and the sensor is a generic OPT101 monolithic photodiode, common in pulse ox setups. The OPT101 is placed 3cm away from the LEDs to get an average reading of LED light bouncing through the skull and brain surface. This spacing ensures that we are minimizing light reflected from the skin while not being too far to lose the light being
bounced off the brain. The reading is then an average of returned light plus passive infrared (i.e. body heat), as long as all external light is blocked out from the sensor. The Red LED is set at a higher intensity via a lower resistance, this emphasizes the Red over the Infrared and makes changes in ratio more obvious without filtering.

The analog-to-digital converter (ADC) is an ADS1115 16-bit ADC with a Programmable Gain Amplifier (PGA). The ADC functions at up to 860 samples-per-second (SPS) with 32767 steps, and a step resolution of about 0.125mV at max gain. The LED light from the sensor provides plenty of signal for the ADC’s fairly rough resolution to detect on top of the body’s passive IR/heat. Up to 4 ADS1115s can be used in parallel with 4 channels each. We can upgrade this to an ADS1256 for example, which has 24 bits available and a 30kSPS sample rate and 8 channels, more ideal for simultaneous multi-sensor setups and gathering clinical data.

The microcontroller simply requires an I2C input for these types of ADCs and preferably a serial output, whether via USB or wirelessly via WiFi or Bluetooth. The most affordable microcontrollers out there, like the ATmega328P-based Nano v3 - found for less than 2 dollars a pop on Aliexpress - have enough horsepower to take all the readings necessary at our sample rates. The ESP32 can handle these readings plus a WiFi, Bluetooth (including BLE), or USB output. The Bluetooth response rate is restricted on the ESP32 in the arduino libraries to 10ms, but one can send arrays of amassed data in those periods to compensate for the bottleneck, or work around it with the standard C libraries. Arduino, or even Raspberry Pi, provide ideal starting points for newcomers in hardware and for setting a minimum bar for commercial production.

Code

Available on github. (https://github.com/moothyknight/HEG_ESP32)

Code breakdown of HEG_BTSerial.ino for ESP32 arduino boards as of 3/7/2019. The code has since been updated but this will explain functionality This code and walkthrough are geared for novices. It won’t cover every line but the code itself is well-commented and self-explanatory if you follow the logic. Using Visual Studio Code in images.

Required:
ESP32-based Arduino board. Recommended: Wemos or Adafruit brands, lots of options. Arduino IDE (https://www.arduino.cc/en/Main/Software)
ADS1X15 library (https://github.com/adafruit/Adafruit_ADS1X15)
Arduino_ESP32 library (https://github.com/espressif/arduino-esp32)

Lines 23-30


Set default settings whether you want to use USB or Bluetooth input/output, or both.concurrently. These can be toggled via command, too, but you need at least one active by default. The last setting is whether you want to enable pIR mode or not, which is experimental at the moment but requires no LEDs, as pIR is merely correlating passive body heat with metabolic activity.

The different Debug bools are helpful in the arduino IDE, to let you check out different values in the serial monitor and plotter.

One more notable value is SEND_DUMMY_VALUE. This will send random values in the same string format as the real data so you can simply test throughput. Not shown, setting sensorEnabled to true will have the sensor run upon powering the device by default rather than requiring toggling with ‘t’/’f’.

Lines 38-40

Set pins for the RED and IR sensor LEDs. The third LED setting is if your ESP32 board has an indicator LED, as demonstrated on the Lolin32. Pins 13 and 12 are the chosen defaults for the Lolin32 and Huzzah32 setups.

Lines 97-101


These are the timing variables (in milliseconds) for the various timed events. ledRate sets the flash alternation rate. Currently this code is set to flash between Red and Infrared with no rest period where both LEDs are disabled, which is recommended to get a baseline adc reading that can be subtracted as noise from the LED signal. It is not necessary to see changes expressed, as ratio to blood-oxygen is on a nonlinear scale anyway and the ADC is plenty sensitive to pick them up on top of the body noise.

sampleRate is the rate at which the ADC takes readings. The ADS1115 max read rate is 860 samples-per-second or 1/860 seconds per tick. We set it to 1.5 milliseconds for about 667 samples per second, which is more than enough. Samples for each LED are averaged over the period of each LED flash. This averaging reduces noise and lets one take full advantage of the ADC.

samplesPerRatio is the minimum number of samples for each LED flash required to take a ratio. We recommend setting it based on a full flash cycle.

BTRate is the Bluetooth transmission rate. It’s set to 100ms by default, can go to 10ms in the Arduino IDE, while it should be able to go much faster through the C libraries provided by Espressif, which are much harder to code with. 100ms is plenty for user interaction, while USB data transmission is always as fast as the sample rate. Bluetooth data is averaged before sent, in case 2 or more ADC or ratio readings are taken per Bluetooth interval. This allows variables to be changed arbitrarily while minimizing loss. USBRate default set to 0 as delay is not needed unless on slower computers.

Lines 104-117


The startADS() function begins the ADC reading and sets the gain to the maximum. The program and LED timers start at this moment, too. For boards without pre-set SDA and SCL pins, you can use Wire.begin(SDA,SCL) instead of ads.begin().

Lines 119-162
commandESP32()
We are using simple 1 character commands over full strings. This is easier to deal with when using BLE instead of a serial profile. Commands are:

t = enable sensor and HEG program
f = disable sensor and HEG program
r = reset baseline and ratio readings
p = pIR mode. Disables LEDs basically
u = toggle USB output
b = toggle Bluetooth output
0-3 = Sending ‘0’ thru ‘3’ will change which of the 4 channels the ADS1115 is using.

Lines 164-178


One of the default functions for arduino. This sets up GPIO pins and begins advertising the bluetooth server. The default name for Bluetooth pairing is “My_HEG”, which will show up upon scanning for devices on phone or laptop.

Lines 181-188


The core_program() contains the essential HEG code. It begins when the sensorEnabled bool is set to true. The program then checks if the adc is enabled and enables it, then begins reading the ADC. After the ADC is enabled, the LED flash sequence will begin, followed by sampling.

Lines 192-228


LED alternating sequence, contains commented out code to add a third no-LED sequence. Change ledRate to change the interval period for the LEDs, in milliseconds per LED

Lines 230-268


If the sampleRate time has elapsed, the device reads the ADC on the I2C channel. If the adc signal is over 3000 or the reset flag has been triggered, the ratio scoring and baseline will be reset. This ensures that there is a rough margin for bad data. If the signal is under 3000, the badSignal flag will be set to false and the baseline will begin accumulating.


Lines 269-289

This section is for determining a baseline value, which is used to compare a position change. After the badSignal flag is set to false, the device waits for 250 samples (to allow time for the sensor to settle) then accumulates 250 samples of each LED. There is a commented out extra option for comparing ratios after subtracting non-LED data out. After the sample quota is met, signalDetermined is set to true and the initial baseline ratio is calculated.

Lines 290-314

Ratio is taken by dividing the logarithm of the Red light average (accumulated red samples / number of sample ticks) by the logarithm of the IR light average. The log scaling is not necessary but was recommended in a pulse oximetry paper [15]. We observed it slightly improved emphasis in ratio changes but reduces the range of variance. This might be removed later. The bratioAvg value, badc0, and bposAvg values are separate for bluetooth data, as it uses averaging to minimize loss over a slower transmitter interval.

Lines 315-340


After baseline is achieved, the regular ratio-taking interval kicks in. The minimum samplesPerRatio should be however many samples happen over a single LED flash. The ADS1115 can get more than 20 samples per flash, although we are functioning closer to 6 samples per flash, and our default minimum is set to 5 samples required. This is ample for scoring at a 20Hz LED rate. posAvg tracks the slope of the ratio changes from baseline, providing a simple way to track changes over time. This can be used to calculate “velocity” and “acceleration”derivative curves for additional metrics. posAvg / time between p1 and p2 = “velocity.” “velocity” / time between p1 and p2 = “acceleration.”

There is more commented-out code below this screenshot that is not shown, useful for debugging.

Lines 370-394


After a ratio is taken, the LED sampling ticks and values reset, the sampling timer is updated, and the adcAvg with paired sampling ticks value accumulates the next reading.

Lines 410-479
The bluetooth() function controls information being sent via the Bluetooth-Serial port. It triggers every time the BLE interval passes. There is a bottleneck of 10ms for the bluetooth signal in arduino. The string format sent is “ADC,RATIO,POS”. While baseline and intermediate LED samples are being accumulated, the RATIO will read “WAIT” and no POS value will be reported. If SEND_DUMMY_VALUE is true the dummy string is generated on line 542. This lets you test computer or phone-side bandwidth easily without needing to assemble the HEG.

Lines 482-556
The usbSerial() function is essentially the same as the bluetooth() function minus the 10ms bottleneck.

Lines 558-573
checkInput() checks if any single char commands have been received over serial or bluetooth.

Lines 575-588
loop() is the default core loop for arduino scripts. On the ESP32 it automatically distributes work between cores. The core program, input checking, and usb and bluetooth transmission are handled here. The 1ms delay is placeholder as not having it blocks input checking.

HEGstudio modification
Our HEGstudio scoring code via modded exe or parsers.py in the source, available on github: (https://github.com/moothyknight/HEG_ESP32)


The scoring on HEG studio for our device is more of an “effort” score than an objective ratio, though it follows the ratio changes accurately. The scoring is simply a shorter-interval simple moving average minus a longer-interval simple moving average for the incoming ratio readings, added to the previous score, with some extra padding for noise and a multiplier to exaggerate changes. Raw light ratio changes are within the 1% to 5% range before applying the log10 scaling, which correlates to a full range of blood oxygen changes. We need more testing to determine the exact ratio to SpO2 relationship on our setup. This provides smoothing while still being reactive to changes as a sort of “effort” value. We don’t know if the other HEG solutions are close to this one, but this is good enough for real-time interactivity while not giving us an objective blood-oxygen ratio scale.


Test Results

Left: ADC results from sensor on forehead with no LEDS.
Right: ADC output showing LED reading differences with sensor on forehead.

ADC output on Arduino IDE with LEDs alternating, sensor on forehead with no light leaking:

IR = higher values, Red = lower values

HEGstudio output using our scoring method:


Tests with about a dozen different users have shown this setup to successfully correlate with user effort. The score increases as the bloodflow ratio moving average increases or decreases. The reported current ratio here is not really the real ratio, as variance by our method is within the +/- 5% range. Our SMA scoring function exaggerates changes and smooths feedback to be more user friendly and responsive. These numbers are while using 220 Ohm resistors which didn’t allow full red LED intensity, which increases the range of variance measured.

Ideal Future Directions

Research
- Establish with data the clinical effectiveness of the HEG for various symptom profiles.
- Also establish standard methodologies and interactivity to better address different symptoms.
- Address ADD [9], Depression [10], PTSD [11], perhaps hallucinations [12], via stimulating and strengthening associated areas of the neocortex.
- Exploring the effects of different types of stimulus on brain-blood flow quality/consistency, like mnemonics, music, games, etc. [13]
- Bring it into more schools and competitive environments.
- Requires careful controls, software is the easiest way to provide these controls (as in providing predictable experiences with different objective outcomes).
- Competitive gamers are an untapped market. Easiest to study, too.
- Geographic data from people walking around with this data, build stress and attention maps from these.
- Get deeper with the operant/classical condition capabilities - but don’t be creepy or evil.
- MORE. DATA. QUANTIFY ALL THE THINGS.

Software
- Desktop Software
- HEGstudio has been modded for compatibility with the HEG arduino profiles we provided at https://github.com/moothyknight/HEG_ESP32.
- Mobile Software
- React Native and Nativescript attempts exist right now with performance issues.
- Unreal Engine and Unity Implementation, and more game engine and game content.
- Will open up rapid prototyping UI and visual/sensory design greatly plus easy cross-platform.
- Tap the competitive gaming market to provide game-integrated stress and focus monitoring or training cues.
- Easy data science visualization.
- Explore brain-computer interfacing and what types of feedback work.

Hardware
- Miniaturize. Cheapen. Miniaturize. Cheapen.
- Keep the open source model up to date with the popular hardware.
- Explore 2D and 3D mapping solutions.
- 3D is the hardest but will create one of the first visible light body scanner type devices. Consider this Star Trek level.

Potential markets:
- 20% of the US population with some kind of mental illness, often go years without improvement or mere recognition of symptoms. [14] Global rates are similar.
- Students and children as a learning tool.
- Self-improvement and bio-hacking enthusiasts.
- Therapists as part of their toolkit (with approval as medical technology)
- All adds up to tens if not hundreds of millions of users.

Conclusion

We want this device to proliferate and have a major impact on how well people can treat their health and get to know themselves. We believe this would make the world a better place and open many more doors for mental health and biofeedback research, as HEG is currently too obscure and specialized for how straightforward and promising the science is. It's also convenient for people who do not have much time or energy to spare to their health, something key to consider in a country where people cannot or will not pay for co-pays or rehab, and general trust of professionals is low due to the dark and inexcusable history of mental health education and treatment in this country.
We’d like to extend special thanks to Eric Nichols, William Croft, Stephanie DuPont, Bob Marsh, Jonathan Toomim, and Peter van Deusen for their support and for the trailblazing they’ve done before this project that made it all possible

Citations/Further Reading:
1. Toomim, H, Marsh, R. “Biofeedback of human central nervous system activity using radiation detection” 1996. USPTO <https://patents.google.com/patent/US5995857A/en>
2. Bentourkia et al. “Comparison of regional cerebral blood flow and glucose metabolism in the normal brain: effect of aging.” 2000. PubMed. <https://www.ncbi.nlm.nih.gov/pubmed/11099707>
3. Dias et al. “Clinical efficacy of a new automated hemoencephalographic neurofeedback protocol” 2012. NCBI PubMed. <https://www.ncbi.nlm.nih.gov/pubmed/23156903>
4. Gomes et al. “Hemoencephalography self-regulation training and its impact on cognition: A study with schizophrenia and healthy participants” 2017. NCBI PubMed. <https://www.ncbi.nlm.nih.gov/pubmed/28882685>
5. Marzbani et al. “Neurofeedback: A Comprehensive Review on System Design and Clinical Applications” 2016. NCBI PubMed. <https://www.ncbi.nlm.nih.gov/pmc/articles/PMC4892319/>
6. Rakic, Pasko. “Evolution of the neocortex: Perspective from developmental biology” 2009. NCBI Pubmed. <https://www.ncbi.nlm.nih.gov/pmc/articles/PMC2913577/>
7. Galynker et al. 1998. “Hypofrontality and negative symptoms in major depressive disorder.” NCBI PubMed <https://www.ncbi.nlm.nih.gov/pubmed/9544664>
8. United Nations. “UN health agency reports depression now 'leading cause of disability worldwide'” Feb 2017.
<https://news.un.org/en/story/2017/02/552062-un-health-agency-reports-depression-now -leading-cause-disability-worldwide#.WLRpQBB3xBw> (https://news.un.org/en/story/2017/02/552062-un-health-agency-reports-depression-now-leading-cause-disability-worldwide)
9. Sharma, Anup et al. “Non-Pharmacological Treatments for ADHD in Youth” 2016. NCBI PubMed. <https://www.ncbi.nlm.nih.gov/pmc/articles/PMC4968082/>
10. PA. “Schizophrenics learn to silence the voices thanks to MRI scanner, game.” Feb 2018. The Sydney Morning Herald. <https://www.smh.com.au/world/europe/schizophrenics-learn-to-silence-the-voices-thank s-to-mri-scanner-game-20180212-p4z00t.html> (https://www.smh.com.au/world/europe/schizophrenics-learn-to-silence-the-voices-thanks-to-mri-scanner-game-20180212-p4z00t.html)
11. Toomim, H., Johnson, R. “Anxiety, Anger, Depression, TBI and HEG” Nov 2009. Futurehealth.org
<https://www.futurehealth.org/articles/Anxiety-Anger-Depression-by-Hershel-Toomim-09 0723-101.html> (https://www.futurehealth.org/articles/Anxiety-Anger-Depression-by-Hershel-Toomim-090723-101.html)
12. S, Yun et al. “Stimulation of entorhinal cortex-dentate gyrus circuitry is antidepressive” April 2018. NCBI PubMed. <https://www.ncbi.nlm.nih.gov/pubmed/29662202>
13. Dresier M et al. “Mnemonic Training Reshapes Brain Networks to Support Superior Memory” Mar 2017. NCBI PubMed. <https://www.ncbi.nlm.nih.gov/pubmed/28279356>
14. “Mental Health By The Numbers” 2018. NAMI.org. <https://www.nami.org/learn-more/mental-health-by-the-numbers>
15. Lopez, S. “Pulse Oximeter Fundamentals and Design” Nov 2012. Freescale Semiconductor. <https://www.nxp.com/docs/en/application-note/AN4327.pdf> Further Reading:
16. Toomim et al. “Intentional Increase of Cerebral Blood Oxygenation Using Hemoencephalography (HEG): An Efficient Brain Exercise Therapy” 2005. Journal of Neurotherapy Vol 8 Issue 3. <https://www.tandfonline.com/doi/abs/10.1300/J184v08n03_02>
17. Shoshev, M. “Hemoencephalography Neurofeedback - Mechanism of Action” 2017. Trakia Journal of Sciences

<https://www.researchgate.net/publication/323699457_Hemoencephalography_neurofeedback_-_mechanism_of_action> (https://www.researchgate.net/publication/323699457_Hemoencephalography_neurofeedback_-_mechanism_of_action)
18. Zivodar, I. et al. “Neurofeedback application in autistic spectrum disorders” Sept 2015. ResearchGate.
<https://www.researchgate.net/publication/290290548_Neurofeedback_application_in_the_treatment_of_autistic_spectrum_disorders_ASD> (https://www.researchgate.net/publication/290290548_Neurofeedback_application_in_the_treatment_of_autistic_spectrum_disorders_ASD)
19. Gagnon et al. “Improved recovery of the hemodynamic response in diffuse optical imaging using short optode separations and state-space modeling” 2011. NeuroImage Issue 56.
20. Gagnon et al. “Short separation channel location impacts the performance of short channel regression in NIRS” 2012. NeuroImage Issue 59.
21. Saager, R., Berger, A. “Direct characterization and removal of interfering absorption trends in two-layer turbid media” Sept 2005. Journal of Optical Society of America Vol 22.
22. Saager, R., Berger, A. “Measurement of layer-like hemodynamic trends in scalp and cortex: implications for physiological baseline suppression in functional near-infrared spectroscopy” 2008. Journal of Biomedical Optics Issue 13.
23. “Functional near-infrared spectroscopy neuroimaging device to enter scene this year” March 2016. Korea Advanced Institute of Science and Technology.
24. Marengo Rodriguez, F. “Design and implementation of a low-cost near infrared spectroscopy system” 2017. Self-published.
25. Muehlemann et al. “Wireless miniaturized in-vivo near infrared imaging” 2008. Optical Society of America.

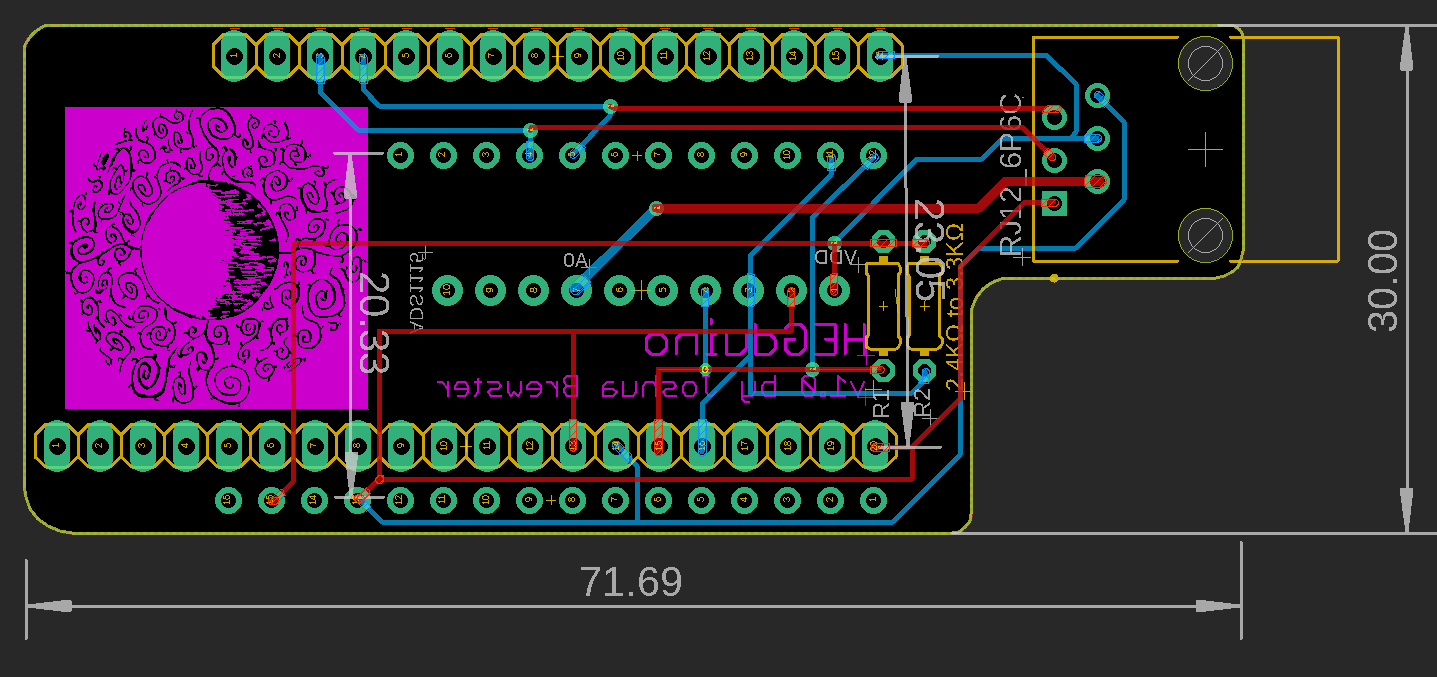
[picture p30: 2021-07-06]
Designs/boards/HEGduinoV1/HEGduinoBrd.PNG

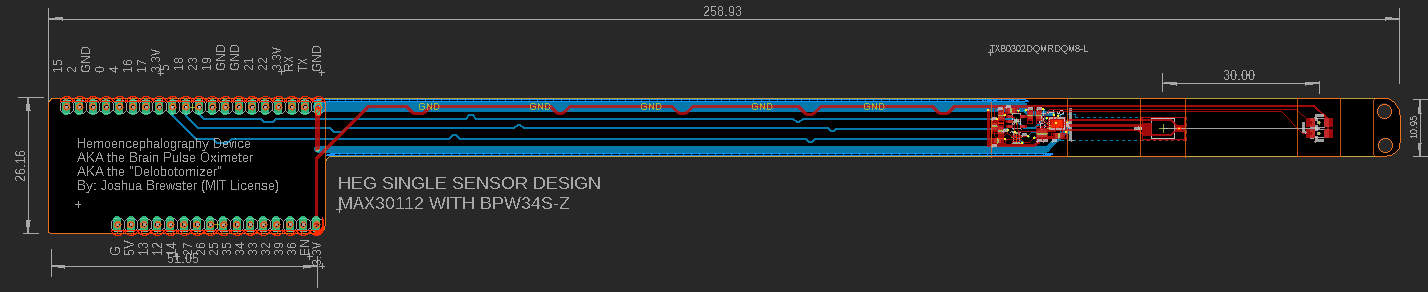
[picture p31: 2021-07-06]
Designs/boards/MAX30112HEG/MAX30112.PNG

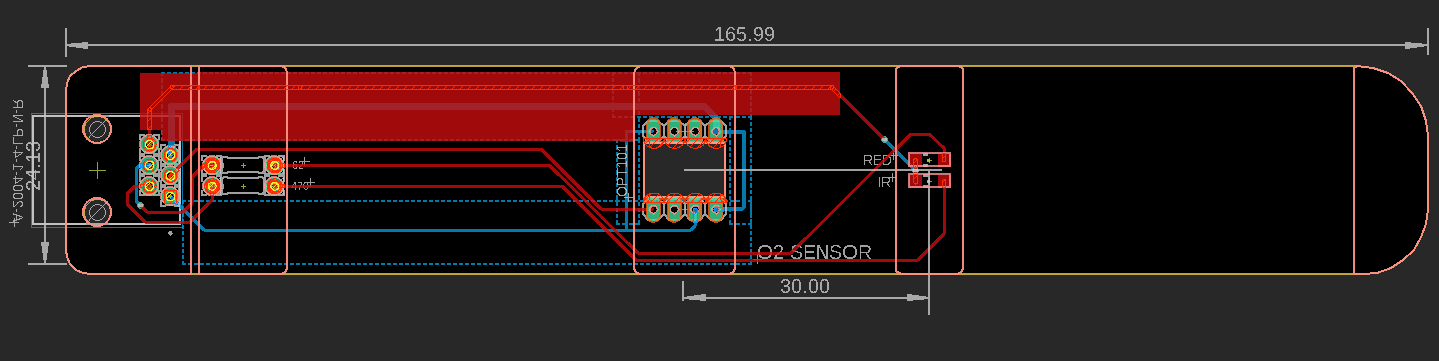
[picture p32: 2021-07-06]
Designs/boards/HEGduinoV1/HEGduinosensor.PNG

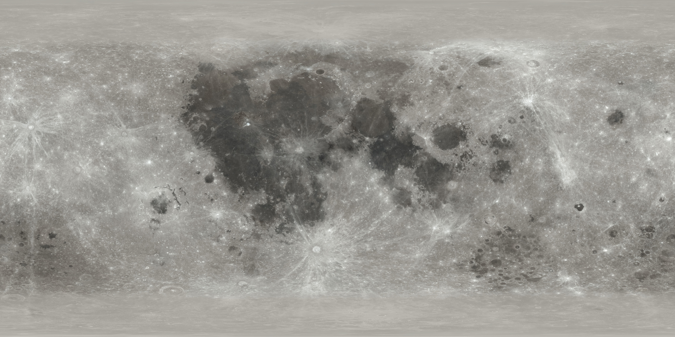
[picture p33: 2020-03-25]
Software/ChromeExtension/assets/textures/moon_4k.jpg

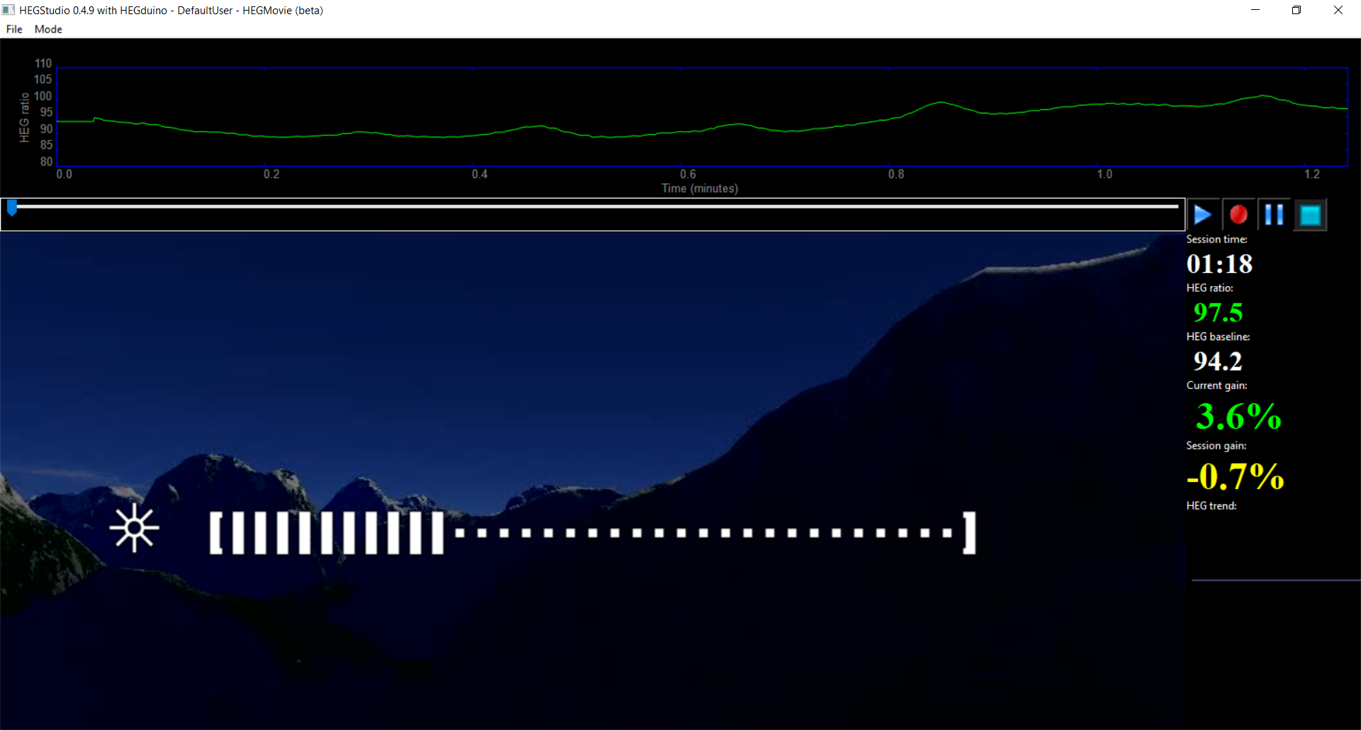
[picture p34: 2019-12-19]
Pictures/hegstudio_with_hegduino.PNG

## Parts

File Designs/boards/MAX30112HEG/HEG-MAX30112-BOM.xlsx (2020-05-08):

Part Key | QTY | Part # | Part # | Digikey Cost by Vol: (can do better) | 1 | 10 | 100 | 1000
U1 | 1 | MAX30112EWG+T |  |  | 6.35 | 57.07 | 467.61 | 3357.2
U2 | 1 | AP2127K-1.8TRG1 |  |  | 0.48 | 3.59 | 17.97 | 103.34
R1,R2,R3,R4 | 3 | 10Kohm Res. | CRGP0402F10K |  | 0.1 | 0.92 | 3.56 | 15.64
C3,C5,C6 | 3 | 10uF Cap. | GRJ155R60J106ME11D |  | 0.22 | 1.51 | 7.66 | 46.37
C4 | 1 | 0.1uF Cap. | C0402C104M9PACTU |  | 0.1 | 0.28 | 1.24 | 6.96
C1,C2 | 2 | 1uF Cap. | C0402C105K9PACTU |  | 0.1 | 0.26 | 1.18 | 6.62
D1 | 1 | BPW 34 S-Z |  |  | 1.11 | 8.65 | 55.63 | 469.76
LED2 | 1 | BR1102W |  |  | 0.48 | 3.41 | 19.88 | 113.62
LED1 | 1 | HAN1102W |  |  | 0.5 | 3.61 | 23.56 | 132.5
U3 | 1 | TXB0302DQMR |  |  | 0.78 | 6.87 | 52.64 | 332.9
 |  |  |  | TOTALS: | 10.22 | 86.17 | 650.93 | 4584.91

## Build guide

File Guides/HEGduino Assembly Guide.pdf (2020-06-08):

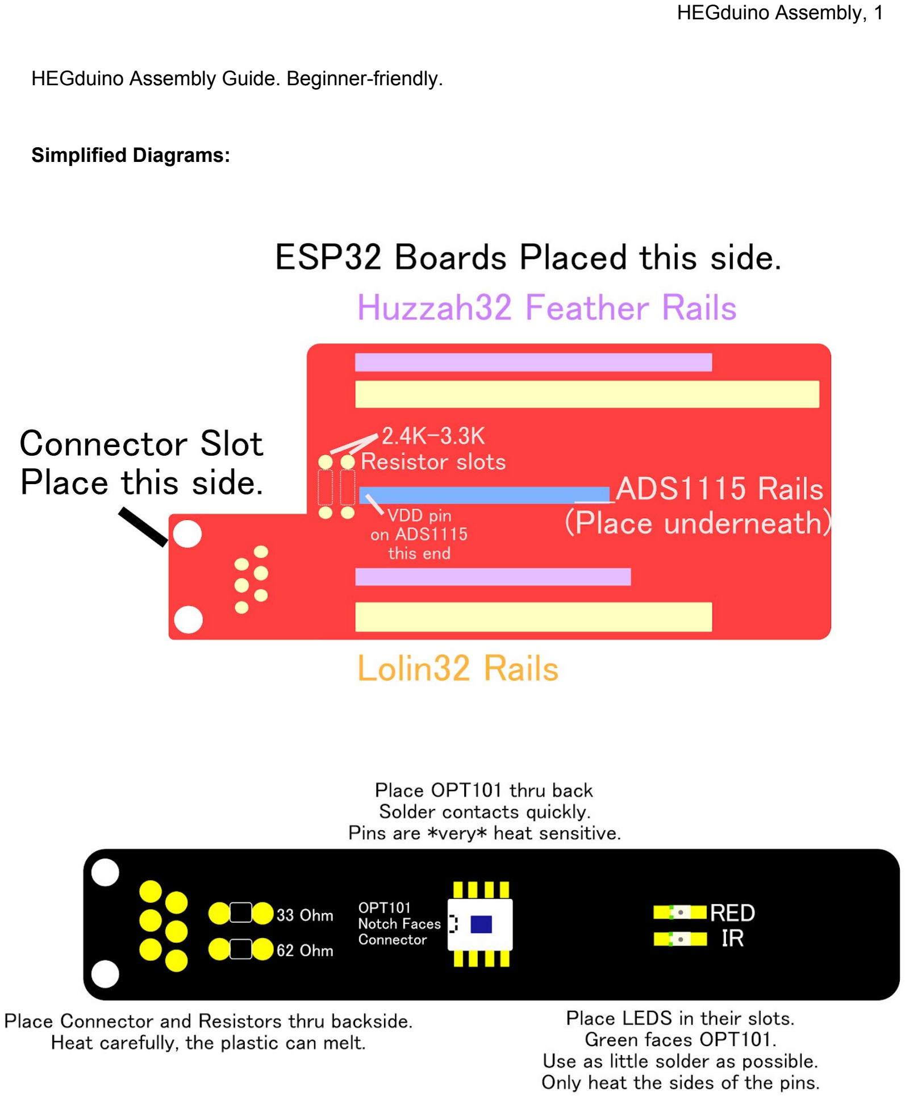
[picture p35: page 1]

HEGduino Assembly, 1

HEGduino Assembly Guide. Beginner-friendly.

Simplified Diagrams:

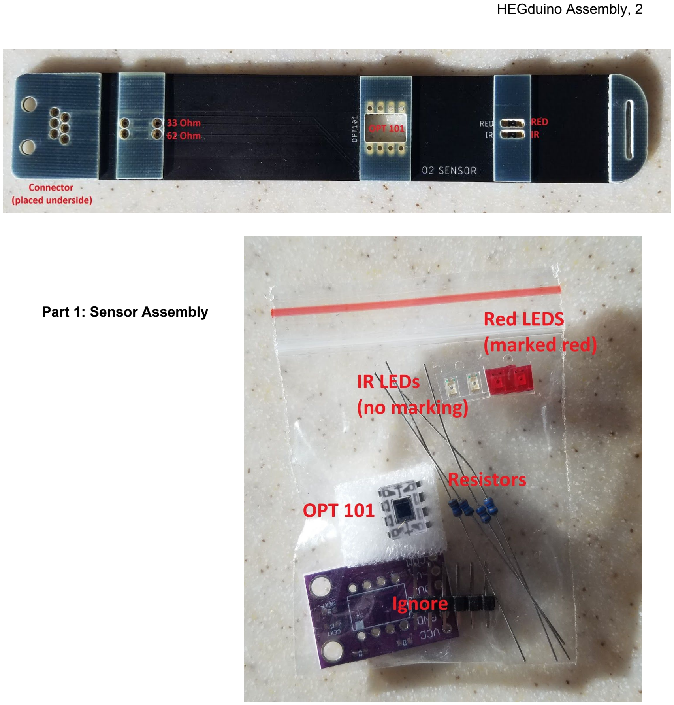
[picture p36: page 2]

Part 1: Sensor Assembly

Sensor: OPT101. *Caution: Solder carefully as it is very heat sensitive* Place the OPT101 through the hole from the backside where the solder pads are exposed. Make sure the notch on the front of the OPT101 is facing the 6p6c connector direction. Solder it down so it is about flush with the stiffener on the face. It’s safest to quickly and very lightly touch the pad next to the pin and place solder wire in-between so it melts onto the pin and pad without you directly heating the OPT101, guaranteeing success much more often.

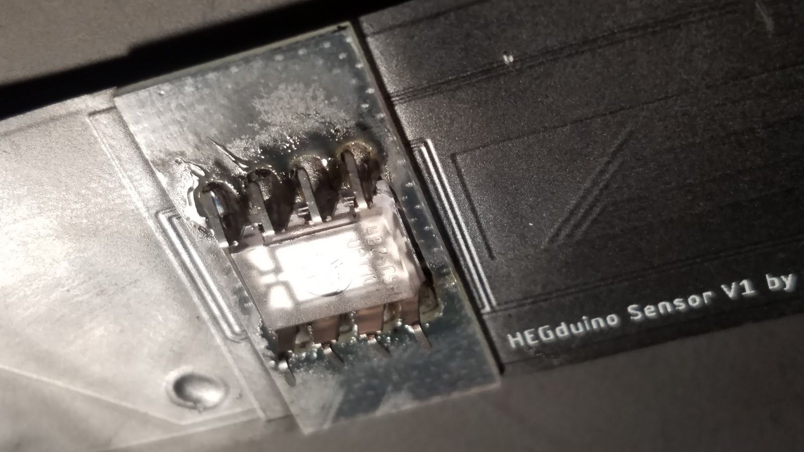
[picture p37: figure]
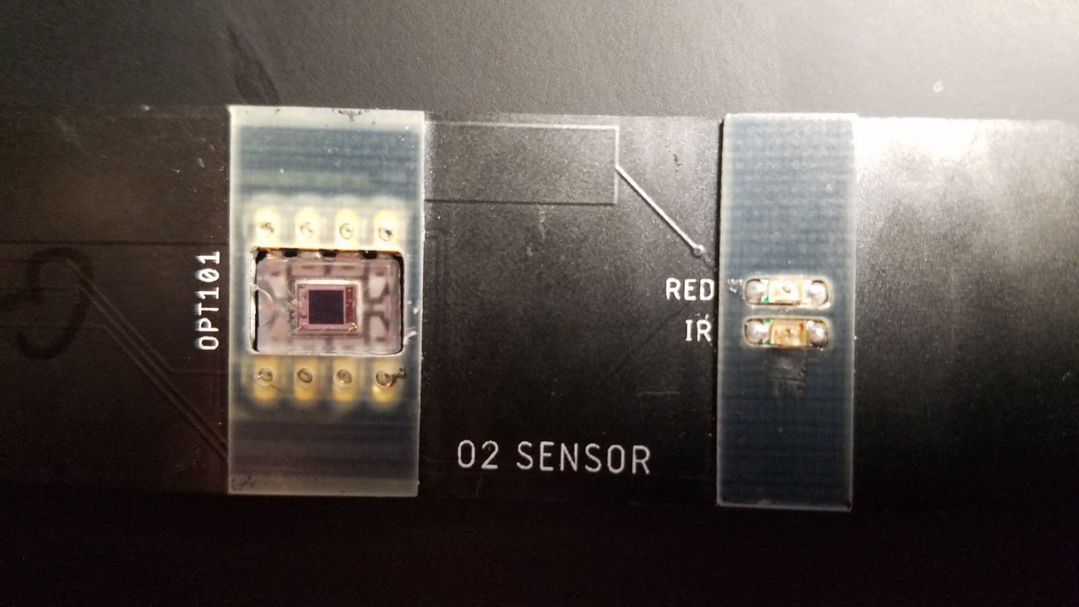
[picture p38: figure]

Sensor: LEDs
The LEDs have tiny green notches on them. Put the Red and Infrared LED in each of their respectively labeled positions with the green notches facing toward the 6p6c connector (direction also marked by little white notches on the PCB). If you forget which LED is which you can always get the Red one to visibly light up with a multimeter set to Diode mode. **Use as little solder as possible and avoid heating the plastic casing around the diode.**

Add the 33 ohm resistor to the 62 spot and the 62 ohm resistor to the 470 spot. We had to lower the resistance on the IR LED due to sensitivity issues that cropped up on lower power settings. Make sure the resistors are on the back side facing away from your head so it doesn't feel awkward. Clip the leads. Finally, add the 6p6c connector to the correct side. You may hold off from adding this connector, as you can also attach the sensor directly to the microcontroller if you want to go wire-free and have a slightly more stable signal.

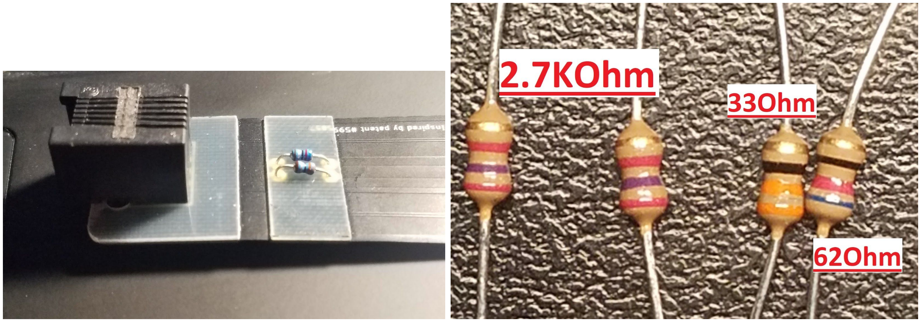
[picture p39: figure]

Finally, use vinyl or rubber tape to cover all of the exposed connections (incl LEDs) as well as the edges of the OPT101 Sensor so it isolates the aperture to be only toward your forehead and prevent light or moisture from the sides or back. You want the metal ring around the dark photovoltaic square of the OPT101 in the clear plastic to be exposed to ensure you are not covering up the sensor with too much tape.

Next page for Part 2.

Part 2: Microcontroller hub assembly

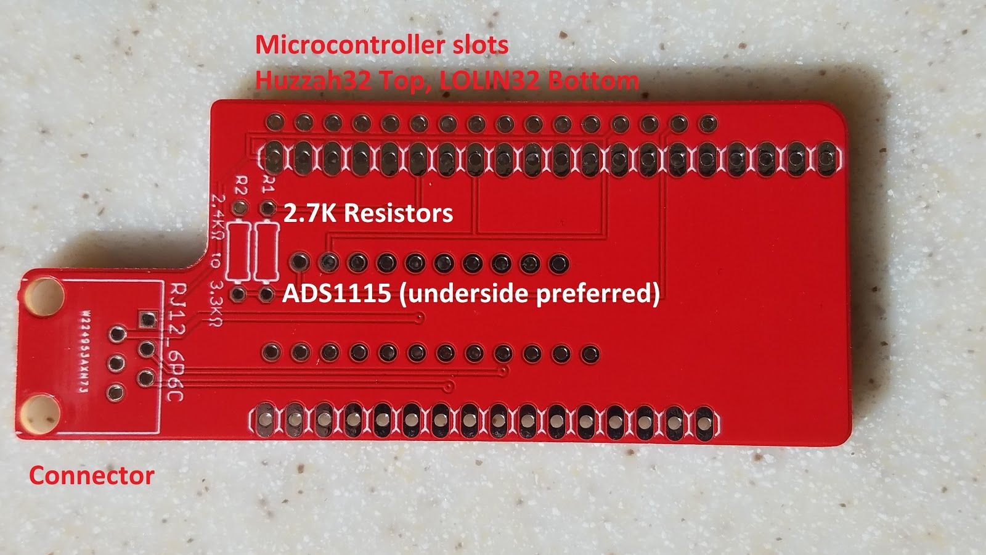
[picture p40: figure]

This part is fairly self explanatory as everything is clearly labeled. First add the 2, 2.7kOhm resistors to their respective slots and the ADS1115. The ADS1115 has clearly marked VDD and A0 pins to indicate the direction it should be placed on the hub board. I recommend putting the pin header for the ADS1115 through the top of the ADS1115 to minimize the form factor. Clip the leads to make room for the ESP32 on the other side. Do this first because it won’t be easy to add these after the ESP32 is soldered.

For a few of you, you’ll have these “V1.1” boards. They won’t have the capacitors and LDO in the kit to go with them yet as these additions weren’t quite working how we wanted yet while there are other minor improvements. The LDO circuit works but did not sufficiently cancel the noise issues we’re finding. Instead, connect the small solder jumper spot near the RJ12 spot for the normal power supply.

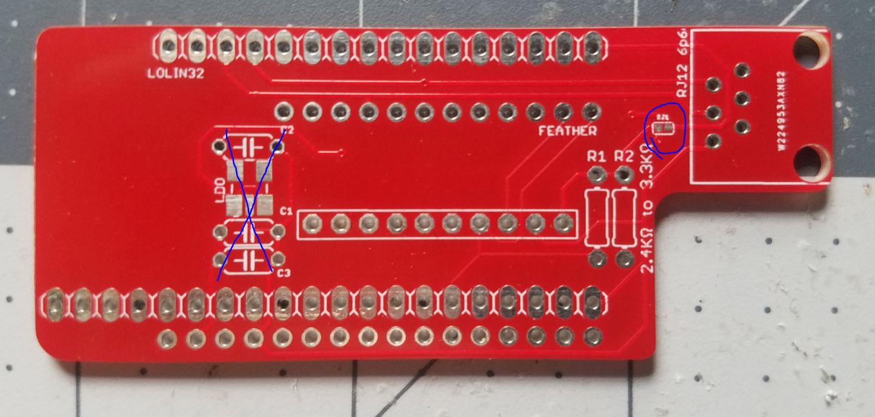
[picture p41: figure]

If you are using a Huzzah32 form-factor board, the ADS1115 comes pretty close to the pin holes (sorry!) but just make sure you’re not completely covering them with the ADS1115. It will work no problem even if there are Huzzah32 pins contacting the edge of the ADS1115 silicon and you are unable to clip them.

After soldering these parts, clip all of the exposed leads as short as possible. There are 2 compatible popular ESP32 boards, the LOLIN32 and Huzzah32 Feather, that only fit in their respective slots on the correct side of the PCB. Next we take care of the connectors.

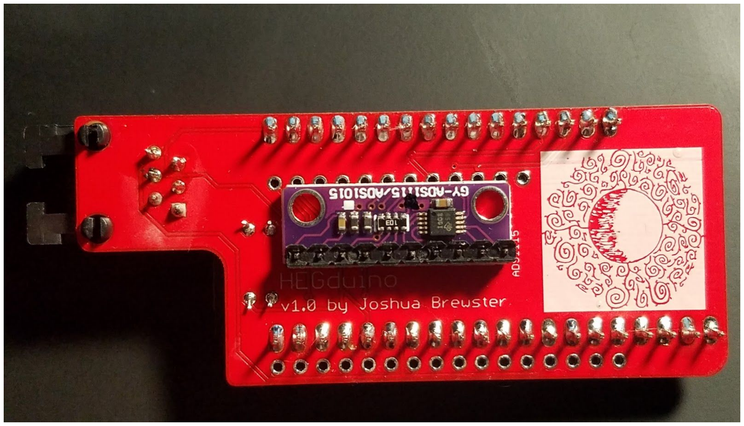
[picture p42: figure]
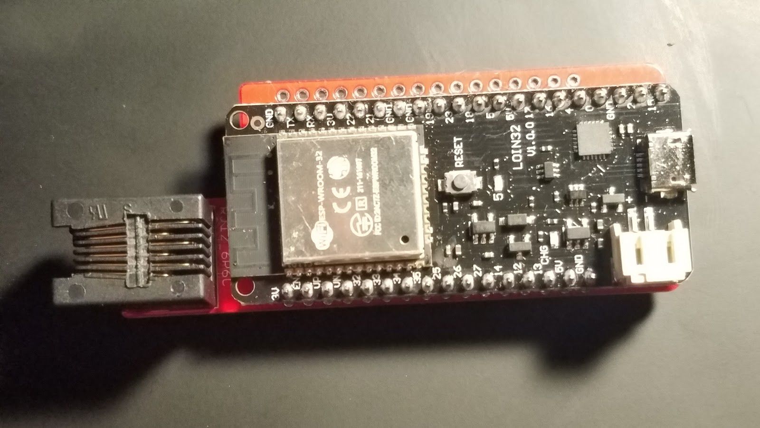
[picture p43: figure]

Connectors
There are 2 6p6c connectors that can be used to give your sensor a cord and make the microcontroller placement more flexible. The pinholes are clearly marked and only fit in one direction.

OR, optionally:
You may also connect the connector pin holes on each PCB together directly on the correctly overlapping side for a shorter but more reliable HEG setup since the cord can be finicky or in the way sometimes. For this you just align the pins so the sensor is facing your forehead and the microcontroller is facing away and use standard pin headers to solder them together.

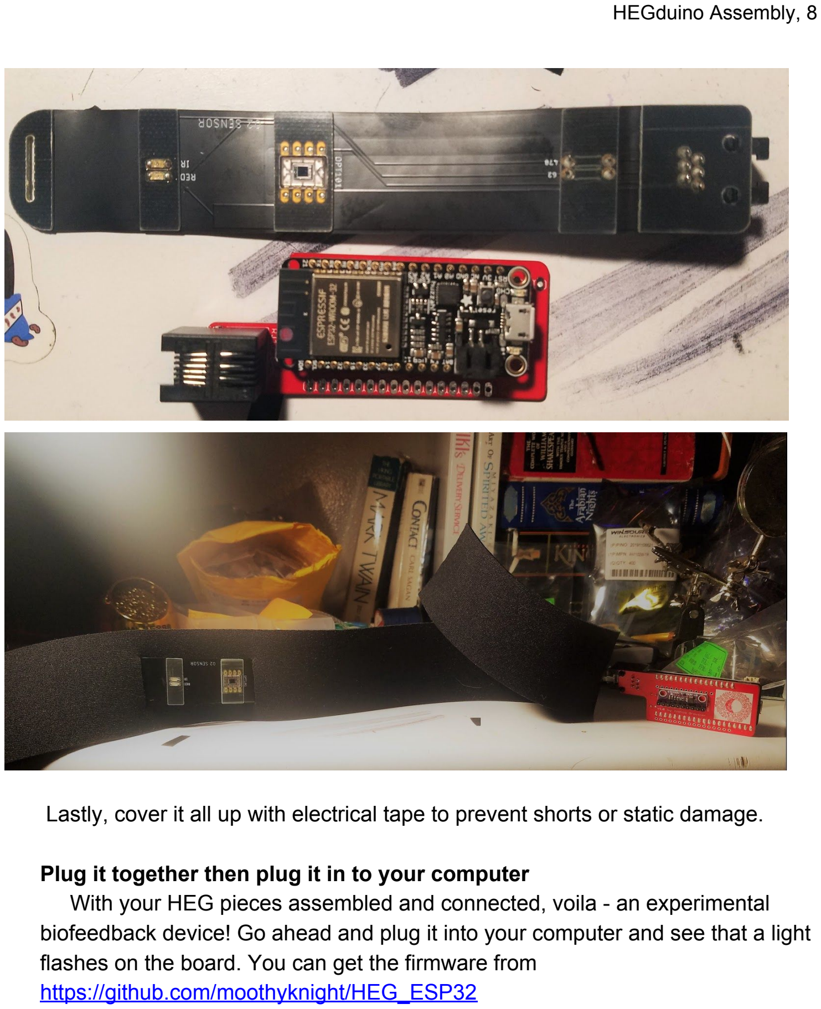
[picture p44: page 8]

Lastly, cover it all up with electrical tape to prevent shorts or static damage.

Plug it together then plug it in to your computer
With your HEG pieces assembled and connected, voila - an experimental biofeedback device! Go ahead and plug it into your computer and see that a light flashes on the board. You can get the firmware from https://github.com/moothyknight/HEG_ESP32

Setting up Arduino
You need the Arduino IDE, (https://www.arduino.cc/en/Main/Software) the ESP32 libraries (https://github.com/espressif/arduino-esp32#installation-instructions) (use the developer libraries rather than the boards manager version so these are modifiable), as well as all of the additional libraries and steps listed in our readme. (https://github.com/moothyknight/HEG_ESP32/blob/master/Device_README.txt)

When that's all set up, if you followed our readme correctly, you should be able to simply open the sketch we provided and hit upload (ensure your Board is selected as well as the partition scheme “Minimal SPIFFS (Large Apps with OTA)”). Check the serial monitor output and try the command "D" to test the sensor and "f" to deactivate it - or just hit the reset button on your board.

After that, you should find SSID "My_HEG" in your WiFi connections list, connect with password 12345678, go to 192.168.4.1 (or http://esp32.local on Apple or Bonjour-enabled devices) via your browser, and check out our on-board demo thanks to the ESP32's awesome web capabilities! Works best on Chrome and Firefox. We now have an awesome Chrome Extension version of our software, too, enabling direct USB support. This is all a work in progress and will be updated for months to come, so keep an eye out by Watching our Github repository!

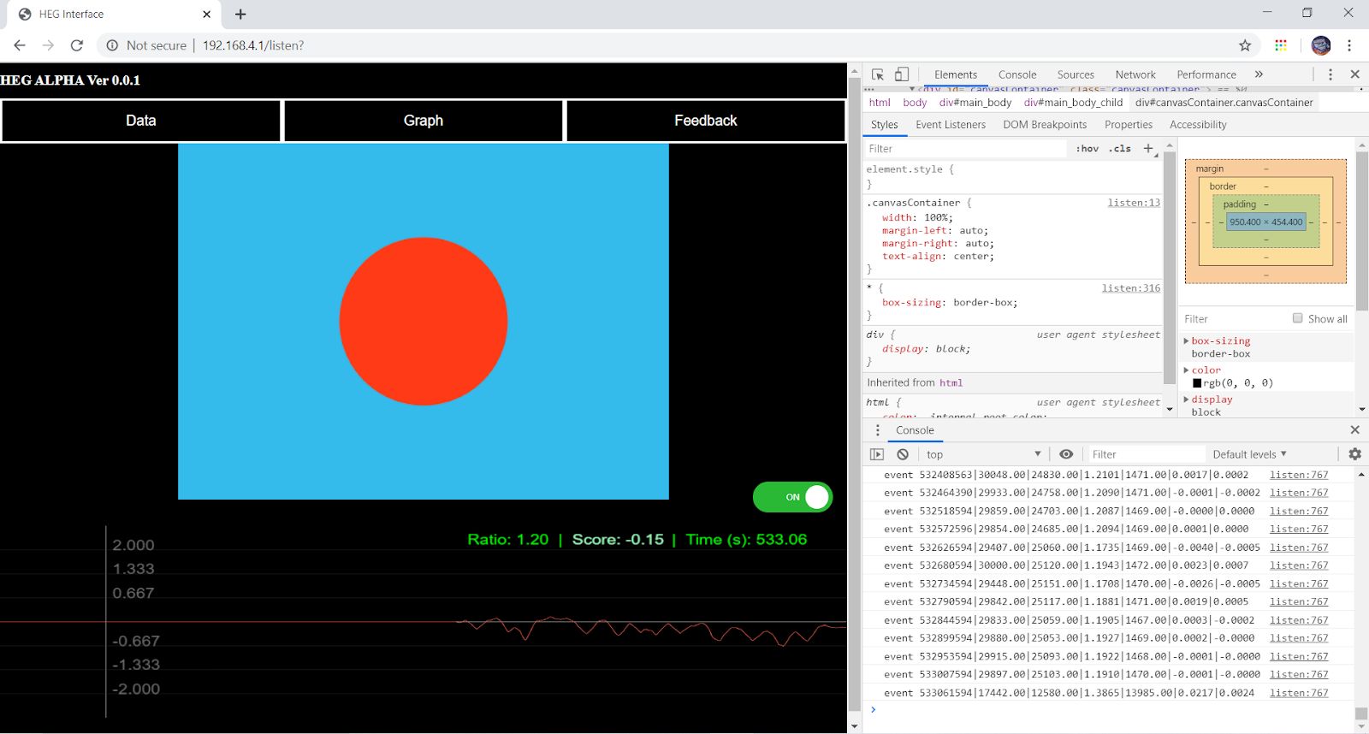
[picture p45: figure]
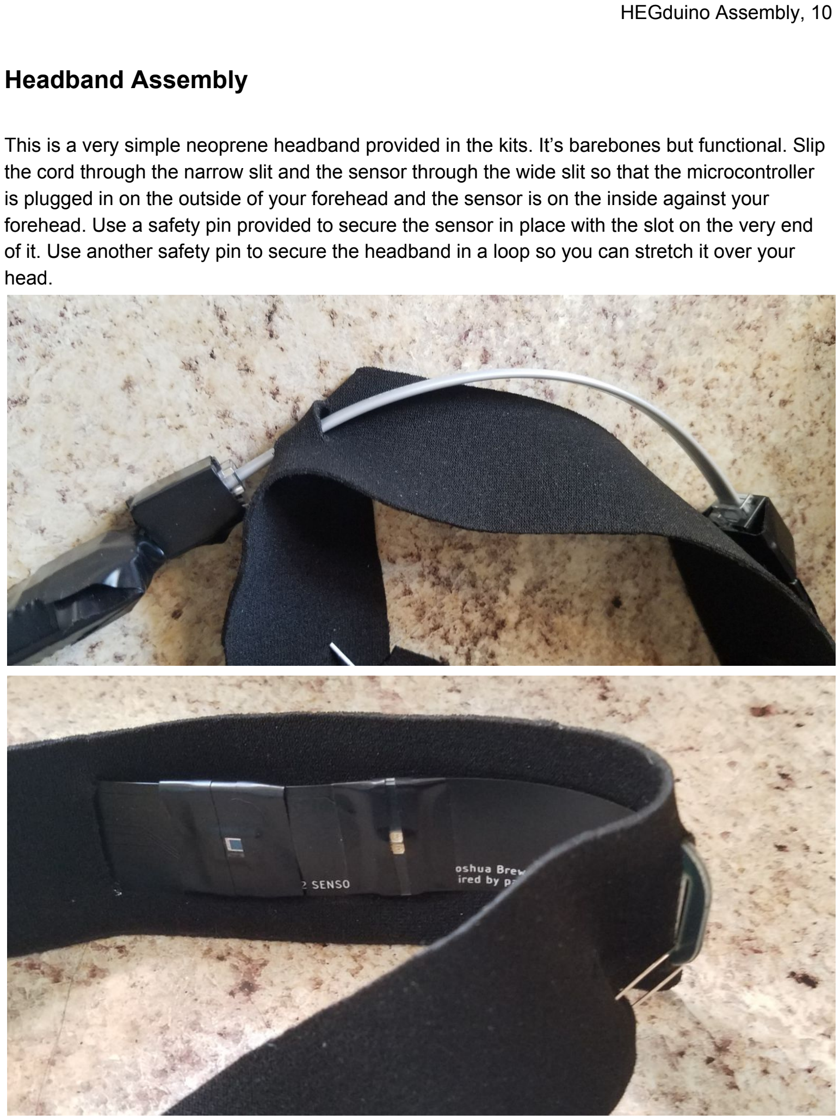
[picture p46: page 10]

Headband Assembly

This is a very simple neoprene headband provided in the kits. It’s barebones but functional. Slip the cord through the narrow slit and the sensor through the wide slit so that the microcontroller is plugged in on the outside of your forehead and the sensor is on the inside against your forehead. Use a safety pin provided to secure the sensor in place with the slot on the very end of it. Use another safety pin to secure the headband in a loop so you can stretch it over your head.

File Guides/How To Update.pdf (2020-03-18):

HEGduino
Quick-update guide.
Step 1: Download the latest update file, which is a .bin file. It is available in the github repo here: https://github.com/moothyknight/HEG_ESP32. Find the .bin update file for your respective ESP32 board in the Device Drivers folder and download it.
Step 2: Connect to your HEG's WiFi signal “My_HEG” with password “12345678”
Step 3: In a web browser (preferably Chrome or Firefox), enter the address “192.168.4.1/update” to come to the update page.

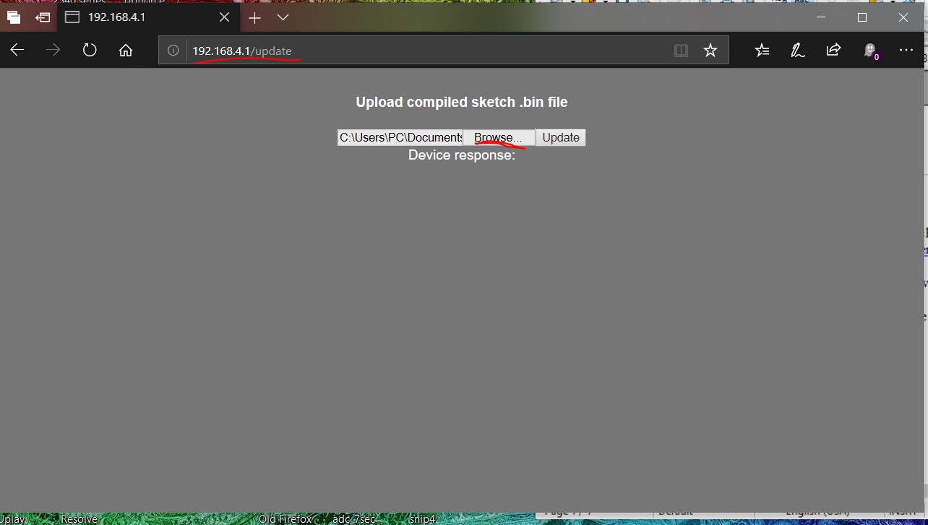
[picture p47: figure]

Step 4: Press the Browse button and find the downloaded update file
Step 5: Press Update. Wait a few minutes as it should freeze up while updating. You should see a progress message.
Step 6: Reconnect and test your output via the HTML5 Demo from “192.168.4.1” in the browser, you can check the Console of your browser to see if the signal is outputting correctly if nothing shows up in the data table. Right-click the page and press “Inspect” or “Inspect element” to bring up your side console. If the console tab is not selected, select it to see an output stream (image on next page)

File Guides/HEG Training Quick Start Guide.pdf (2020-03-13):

HEG Quick Start, 1

HEG TRAINING QUICK START GUIDE

Step 1: Power up your HEG device via the microUSB port or battery port.

*Important* Some power sources can add noise and ruin the signal fidelity. For instance, powering my laptop from a specific wall plug in my room and the HEG from my laptop creates a noisy signal, then it disappears when I unplug it - due to interference from the power port in the wall.

### Step 2:

On your laptop or phone:
- Scan for WiFi signals until you find “My_HEG” listed.
- Connect with password “12345678”

### Step 3:

From your preferred internet browser (works best on Chrome or Firefox):
- In the address bar enter http://192.168.4.1 (or click this link if viewing digitally).
- If that doesn’t work or if on an Apple product, try http://esp32.local.
Step 4: From the main interface page that shows up, select “HTML5 Web App”

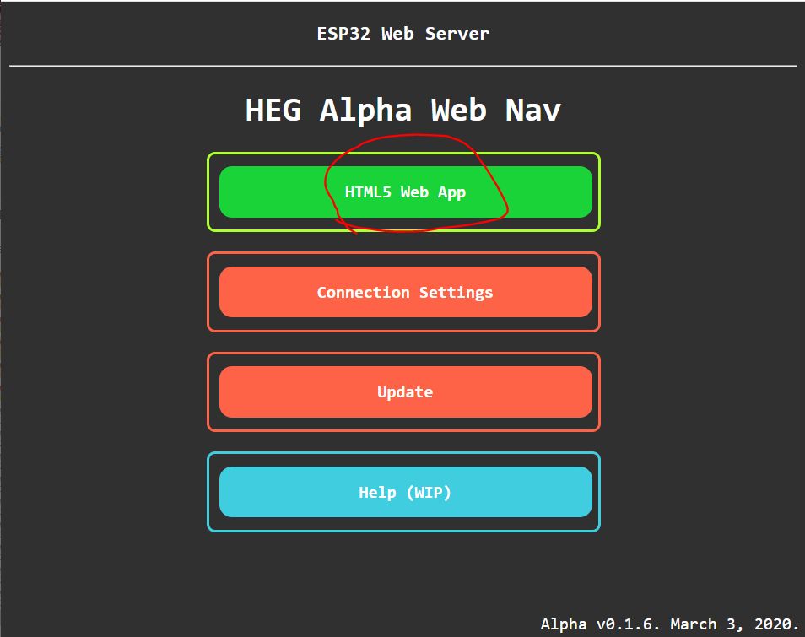
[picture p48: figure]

HEG Quick Start, 2

Step 5: Click the Red slider that says “OFF” to turn the sensor ON.

This should cause the sensor LEDs to flash and for a data stream to come through. You can right click on the page anywhere and click “Inspect” in the menu that pops up to see the data stream.

For a quick exercise, try taking slow, deep breaths for several minutes, and see how that correlates with the information on screen.


Step 6 (optional):
- Click on the Data menu after accumulating some data on the graph.
- Click “Save Data” to save a csv file with your data.
You can also replay CSVs via the Replay CSV button, it will ask you for a file formatted like the ones it saves. If it doesn’t replay on the first try of the button, try again.

Other Notes:
- A highly fluctuating score indicates one or several things:
- The headband is not fully secure against your forehead to block out external light or side light bleeding in from the LEDs: Try to smooth out or reseat the headband on your head so it’s completely flush against your forehead like a piece of tape.
- The power supply or USB wire is corrupting the signal. Try different power sources and different wires. Proximity to WiFi routers and other wireless power sources may also impact noise levels.
- There is moisture on the OPT101 connections: Make sure your tape is secure, you can also add screen protector or clear plastic to improve the waterproofing.
- Your forehead is contacting a connection: Again, check that the tape covers everything.
- The Help page has WIP documentation on various signal issues by the numbers it reads out.

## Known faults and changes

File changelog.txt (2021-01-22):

*-*-*-*-*-*-*
Changelog:
*-*-*-*-*-*-*
1/21/21
------
- Noise B gone! Implemented notch and low pass filtering (3x 50Hz notch,3x 60Hz notch, and 3x 40Hz low pass). AC will never bother you again. I should up the output sampling rate again.
- MASSIVE upgrade to the software incoming.
- 'F' command toggles filters. 'X' command toggles a DC filter. 

11/5/20
------
- Now the indicator flashes happen on the Red LED, I don't know why this didn't occur to me earlier.
- Fixed event source spitting out repeat data

10/31/20
------
- Boids update, new feedback mode with flocking sim.
- Some CSS updates

10/25/20
------
- BLE fixes for android, found one error in the command module causing it to reset. Testing installable PWA implementation (see it at: https://hegalomania.netlify.app).
- new "o" command puts the HEG in fast output mode, so it gets under the android 20 byte/packet MTU limit. This is implemented in the pwa to make it a bluetooth app.

10/23/20
------
- Convenience update! Device now flashes on boot (LOLIN32 only) and lets you toggle different things just with the reset button. The first flashes are in rapid succession. 2 flashes = BLE mode, 3 flashes = WiFi mode, 4 flashes = BT Serial (classic) mode. Then the device will give 3 slow blinks (once per second) after that.
- If you press the reset button again within the first 3 seconds (1 flash per second) that triggers different things.
- Press after rapid flashes and before first slow flash (first second): places device in deep sleep mode.
- Press after first slow flash, before second slow flash: (2nd second: change the communication mode (rotates between BLE, WiFi, and BT Serial)
- Press after second slow flash, before third slow flash (3rd second): wipes saved wifi credentials in case there is some issue.

- BLE connectivity added to extension. Now developing progressive webapp for mobile. 

7/16/20
------
- Generalization: One-liners and commands to control device stream format compatibility e.g. different delimiters and ratio or timer positions, this auto propagates to the CSV recording as well.
- Other cleanup, getting ready for more feature updates.

6/2/20
------
- reverted CSV function in HEGwebAPI (it has the new one too, just not dumping raw data due to noise issues)
- fixed Chrome extension csv printing for serial and bluetooth

6/1/20
------
0.0.10
- Reworked audio system for the AudioJS, fixed the audio feedback (not sure how I broke it!)
- 2 more audio visualizers
- better colors on CircleJS
- tweaked Hill Climber
- Generalized the CSV function
- SoundJS has a recording function you can use, default set for audio recording but can do video, requires a SoundJS class to be set (either when audio is active or through the console)
- SerialUtils.js for the Chrome Extension now has recording and monitoring functions (the monitor is not set up yet on the front end)
- Separated the javascript on the webDemo.html into initWebapp.js for parity with the Chrome Extension
- geolocateJS created for an interesting project

TODO: 
- Make performant serial monitor front end, 
- geolocate.js interactive features - heat maps!
- work on BCIjs integration for EEG data (I need to get ahold of one with a generic data stream) on extension, 
- more visuals, 
- better recording menu.

5/26/20
------
0.0.9
- Added a Sound scripting system, allows arrays of frequencies and sound files to be buffered and used individually.
- Added sound options to HillJS and CircleJS, just simple tones to help indicate the feedback.
- Added a new mode to HillJS, it looks a lot nicer now.
- Some minor fixes

5/1/20
------
- Fixed BLE output format, optimized general output method

4/3/20
------
- USB only mode introduced via command 'u' or toggling on the Connections Settings page at 192.168.4.1/connect or esp32.local/connect
- Fixed the autoscaling on negative graph values (there was none, oops)
- General stability testing, everything seems OK, get your device up to date!

3/28/20
------
- Tooltips!
- New Video mode, control the current time of the video just like HEGstudio! It's officially obsolete. No sound in this mode, but it would probably sound pretty bad.

3/26/20
------
- Fixed the HTML5 page code (didn't paste it correctly)
- Added sleep mode, now the device shuts off after 10 minutes of inactivity. It won't shut off if you are accessing web pages or running the core program, or updating. To turn it back on simply press the reset button or re-plug the power in. This will get more sophisticated to allow remote waking-up.

3/24/20
------
- Reintroduced Bluetooth Serial (surprisingly low footprint on top of BLE). Works like standard USB but requires pairing first. 2 Com ports show up for me when enabled, you want the first one. The one that lets you send commands is the one you want.
- Some bug fixes
- Working on a new video feedback mode
- Separate changelog

3/20/20
------
- Fixed EventSource stream for remote streaming. Updated UI for the changes.
- Added a TextReader feedback option.
- Chrome Extension port of webAPI, with Serial USB support coming. Much easier to code bigger apps in this.
- Microsoft Edge beta supports this UI, and might support the Chrome Extension too.

3/14/20
------
- Added more BLE commands
- Re-added alternative ADS1115 library setup, which is fully programmable up to the full sampling rate (with variable consistency in the data)

3/2/20
------
- Updated SMA function, added basic fault testing for ratio (within 25% error)
- Fixed Annotating
- Some minor tweaks here and there
- DataCharter.html introduced, it's IFrame-ready and meshes with JSON, will soon also be loaded as an online-only option for the firmware. See it in action at hegalpha.com/data (account required)

2/26/20
------
- Fixed yoffset slider (changed a + to a - for the y-axis text)
- Timer now shows minutes and seconds proper.
- Touched up Update page
- Touched up ThreeJS demo colors

2/20/20
------
- Added a formal Reset Session button (instead of reloading page)
- Seconds passed approximation in graph.
- ThreeJS demonstration is even prettier now. 

2/19/20
------
- Added postprocessing fx to threejs demo
- More code cleanup.

2/18/20
------
- Major improvements to code flow
- Conditional ThreeJS integration (auto detects if you are online or not and attempts to add Three.js.min)
- Globe turning exercise to demonstrate ThreeJS and how easy modding is.
- Other minor fixes to feedback and UI.
- Updated env to latest ESP32 release.

2/14/20
------
- Y offset slider
- Fixed fade mode (the CSS needed tweaking)

2/13/20
------
- Exposed method to change event source hosts, for clients not hosted on-board but still on the same network. This opens up more web development capabilities.
- Scoring sensitivity slider can now got to X10, though this is pretty unnecessary.

2/11/20
------
- Graph can now be switched between the score and ratio
- Added Timestamped annotating that will show up in the session CSVs
- Fixed one thing with the x scale slider, the graph crash bug is still there
- Some other API rearrangements

2/7/20
------
- AudioJS options - volume slider and an option for decoupling the volume feedback.
- Fixed HillJS. It's not that great but it's a bit more responsive than before. I need to add more compelling visual feedback.
- Index page update
- Timer actually shows the session time and not the microcontroller clock
- More UI cleanup

2/6/20
------
- Major improvements to UI layout
- API improvements for better generalization (still WIP)
- Custom video controls, show/hide controls
- CircleJS, AudioJS, and HillJS touched up. HillJS is basically unresponsive but I'm working on it next.
- Some cleanup
- IE/Edge will not be supported by the on-board training demos until it is updated to ES8 standards (due to lack of arrow functions, mainly) or until I or others make compatible scripts, still need to test more mobile compatibility as well as understand why some laptops are not compatible.

1/31/20
------
- Minor changes and fixes to UI and javascript

1/22/20
------
- Major mobile-friendly UI updates to web interface page (Alpha 0.0.1 for the interface)
- Changes to data outputs (replaced rSlope and A.I. with velocity and acceleration (voltage units / ms and voltage units / ms ^2). 1 ADC unit = 0.256mV so if Vel = 1 that's +0.256mV gained per millisecond
- Cleanup of HEG.h code.
- Testing notes: 
   -- Some power sources cause unstable readings. Try different power sources.
   -- Different computers/phones seem to have different compatibility errors for the same software (e.g. one laptop not working with Microsoft Edge and another one working great) - not totally sure why.
12/16/19
------
- updated front page, connection page, and help page. Now with version number visible on main page.
- the web API lets you set an arbitrary host for the event source now for quicker remote play (set host with a new HEGwebAPI(parentId,defaultUI,**hostIP**))
 
12/14/19
------
- Made standalone /api page with uninitialized JS api and CSS available for external use.

12/10/19
------
- Rolled back ADC library due to too much instability.

12/8/19
------
- Fixed sampling issues. Now doing 3 samples per LED (and ambient) for 20sps solid over USB, WiFi, and BLE.
- Fixed BLE (thanks Diego!)

12/3/19
------
- Changed ADS1115 libraries to the addicore version (via on i2cdevlib)
- Upped sample rate to 475sps, ratio rate (with ambient cancellation) should now be ~133 at full speed over Serial.
- Fixed Serial commands not being responsive
- Removed "T" test command for now.

11/25/19
------
- fix LEDs not shutting off when pausing HEG
- lowered power consumption
- fixed circleJS in web API

Known bugs:
- Serial USB commands don't register very well 
- ADC anomalies with WiFi (probably power consumption related)
- xOffset bugged when changing xScale and xOffset together

To Do:
- Use a better ADS1115 lib to improve speed
- Web Demo CSS and functionality improvements
- IE and Edge can't find the HEGwebAPI.js script (this is likely the same issue on mobile)

11/11/19
------
- fix web api and hegstudio to match changes

11/9/19
------
- removed sav lay filter (do it on front end instead after checking data)

11/4/19
------
- ADC error check in HEG.h (to deal with a webserver bug), use 'A' to toggle. 
- Add progress events for /update page.

KNOWN BUGS:
The error checker can cause hangups and overheat the chip, don't use it yet

11/3/19
------
-webDemo now filters bad data out for a smoother experience, to compensate for a bug mainly
-testing threading to try to fix wifi data streaming errors. Turn sensor off and on if connecting online while sensor is active. (very particular not often-gonna-happen bug)

Known bugs:
The wifi connection causes errors in the ADC readings for some reason, need to fix this
to make the sav lay filters usable over web.

10/29/19
------
-/discovery page for testing device scanning from mobile
-Reimplemented ambient noise cancelling and added a read_differential mode. Works much better like this, closer to the original!
-/help page (BIG work in progress)

10/21/19
------
-connect page now has a suggest IP option. Return to the /connect page after reconnecting to the access point.
If it works correctly you get booted to the main page and can go straight to the /connect page again, scroll down, and see the suggested info above the wifi scan text.
-proof of concept hill climb game
-more cleanup (not all the way there yet)

More to do:
Audio mode that just plays a tone that gets louder or quieter? 
Device search on local wifi when in STA mode.
More controls for modes.

10/18/19
------
-integrated audio mode
-added volume feedback for video option
-code feng shui improvements

FYI: not all buttons hooked up yet

Known bugs:
-not every browser works on canvas demo
-poor audio quality on visualizer mode - try manual buffering. Bug not present in standalone visualizer.
-offset button bugged when offsetting more than the number of graph vertices (look at xoffsetSlider.onclick setting)

10/17/19
------
smooth mode switching on demo page. Audio and hill climbing (LIFE game re-creation) games incoming.
change graph to show cumulative SMA 1s - 2s slope changes. This math is a simple noise filter that is still reactive to the current information, which can overcome noise issues. 
split code up into multiple files to fit a cleaner traditional webapp format.
web api improving and generalizing rapidly
can set primary/secondary dns if needed, smart config type stuff incoming.

couple bugs:
X offset slider still, it's 3 lines of code causing a problem.
the replay function works fine but goes over the index when resetting the data. This bit will be re-done as the code is spaghetti.

10/14/19
------
-x offset bar. Has a bug when offsetting when graph scale is lower than the array being sliced. page has to be reloaded if red line vanishes.
-Even classier, almost finished streamlining code.
-integrated hegvid code with main page, need to create options to swap once finished generalizing the data handling. this will be smoooooth

10/13/19
------
webGL graphing API improvements. More to come.
WIP Object-oriented web API on canvas demo page. Final suite will be completely class-based.
Sensitivity slider.
/hegvid -> /video (this page will be integrated with the main demo)

More TODO:
Audio visualizer (HTML5 has sweet built-in tools)
CSS Overhaul w/ animations. Utilize webkit/moz/mobile libs.
Fix mobile support for web demo (mostly requires permissions changes)

10/11/19
-----
/hegvid page improvements/experiments. Can load local video files (web URLs next, some site embedding like Vimeo MIGHT work)

10/10/19
-----
CSV Save/Load functions added.
Graphing improved, canvas demo fairly playable now. 
Waiting on new pcbs to get definitive data after fixing noise issues in designs.
GraphJS wrapper class for graphing.

TODO:
graph upgrades
reformat functions and variables into respective classes to reduce bloat.
sliders for exploring data
create SPIFFS js packages? That way we can break up essential functions on the webAPI and reduce bloat or add third party packages easily.
hegstudio brightness exercise recreation is easiest to do with default <video> tag and a transparency overlay.
Fix spaghetti

10/6/19
-----
Fixed crash when changing wifi modes
Add static IP settings. 
Working on WebGL based graphing and video controls. /hegvid wip

10/1/19
------
Canvas demo
Really basic navigation on index page
Fix websocket page to use js to call the hostname in case of esp32.local being used.
More POST commands, also added text input-based command method as an option, only send single char.

9/9/19
------
EventSource works great!

More TODO:
Make connect page notify the user of the new IP address if esp32.local is not fixed.
Convert websockets to drive commandESP32

9/5/19
------
TODO:
Data visualizer. HEG Life game in canvas?
Stress testing - try EventSource instead of Websockets. Websockets can overflow and crash the ESP32 easily if there is lag clientside.
Login interface?
HTML interface to use commandESP32

9/5/2019
------
Fixed OTA, update boards.txt and default.csv in their respective folders (see above install instructions)
Changed setup loop so wifi is always chosen if EEPROM.read(0) is not 1 for BLE.

9/3/19
------
Included BLE support. toggle BLE/WIFI with 'b', BLE default off due to conflict with WiFi
Websockets and HEG now on separate threads so sensor speed is not impacted - WS speed set at 13.33 updates/sec as it's stable. Max = 16/sec
/update broken. Gotta fix it.
Lots of housekeeping to keep workflow easy, tested the freeRTOS threading system a ton.
commandESP32 now in WiFi_API.h.

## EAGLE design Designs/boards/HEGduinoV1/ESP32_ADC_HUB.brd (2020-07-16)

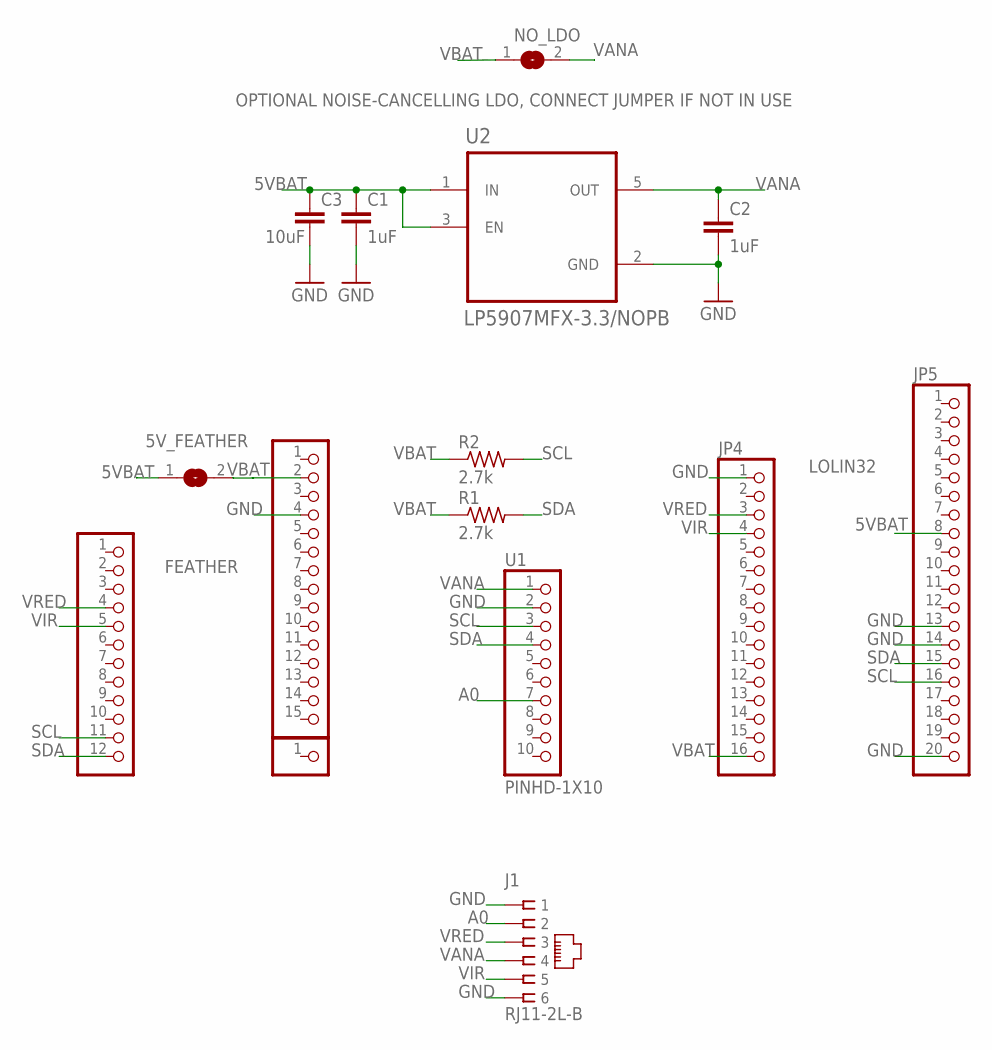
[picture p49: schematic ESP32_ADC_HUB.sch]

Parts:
5V_FEATHER: SJ
C1, C2: 1uF; C050-024X044
C3: 10uF; C050-024X044
J1: RJ11-2L-B; RJ11-NO_SHIELD
JP1: PINHD-1X12-CB; 1X12-CB
JP2: PINHD-1X15-CB; 1X15-CB
JP3: PINHD-1X1CB; 1X01-CLEANBIG
JP4: PINHD-1X16; 1X16
JP5: PINHD-1X20; 1X20
NO_LDO: SJ
R1, R2: 2.7k; 0204/7
U1: PINHD-1X10; 1X10-BIG
U2: LP5907MFX-3.3/NOPB; SOT95P280X145-5N

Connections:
5VBAT: 5V_FEATHER.1, C1.1, C3.1, JP5.8, U2.1 (IN), U2.3 (EN)
A0: J1.2, U1.7
GND: C1.2, C2.2, C3.2, J1.1, J1.6, JP2.4, JP4.1, JP5.13, JP5.14, JP5.20, U1.2, U2.2 (GND)
SCL: JP1.11, JP5.16, R2.2, U1.3
SDA: JP1.12, JP5.15, R1.2, U1.4
VANA: C2.1, J1.4, NO_LDO.2, U1.1, U2.5 (OUT)
VBAT: 5V_FEATHER.2, JP2.2, JP4.16, NO_LDO.1, R1.1, R2.1
VIR: J1.5, JP1.5, JP4.4
VRED: J1.3, JP1.4, JP4.3

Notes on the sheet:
OPTIONAL NOISE-CANCELLING LDO, CONNECT JUMPER IF NOT IN USE
FEATHER
LOLIN32

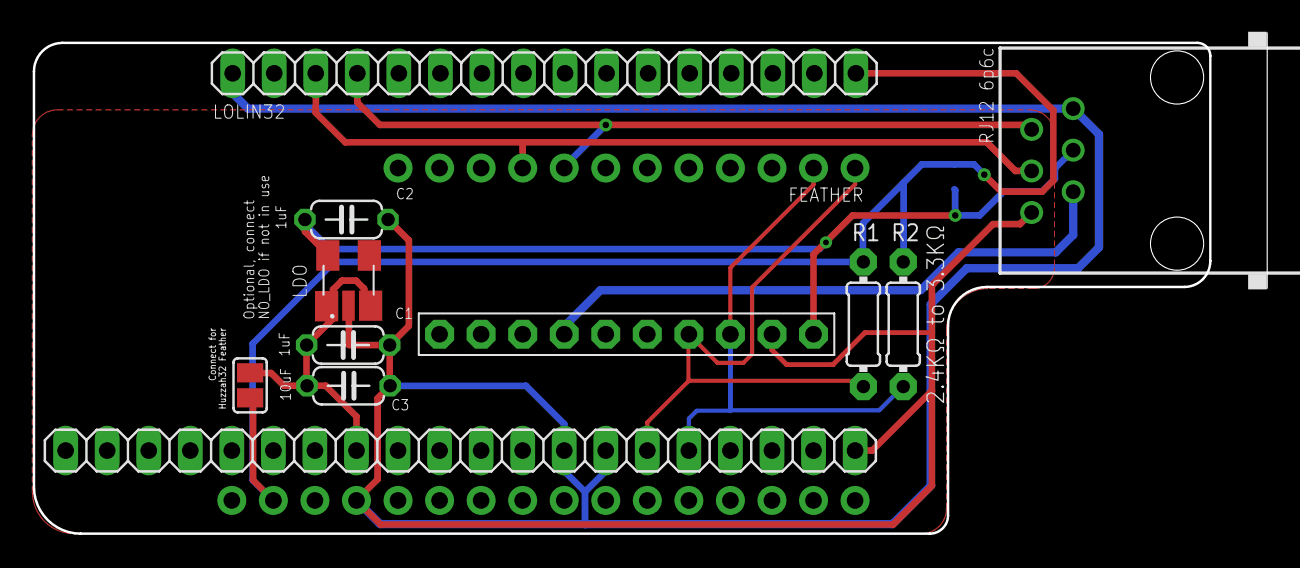
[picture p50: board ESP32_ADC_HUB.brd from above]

Board: 2 copper layers, 75.4 x 30.6 mm, 15 parts (1 on the bottom side), 9 nets.

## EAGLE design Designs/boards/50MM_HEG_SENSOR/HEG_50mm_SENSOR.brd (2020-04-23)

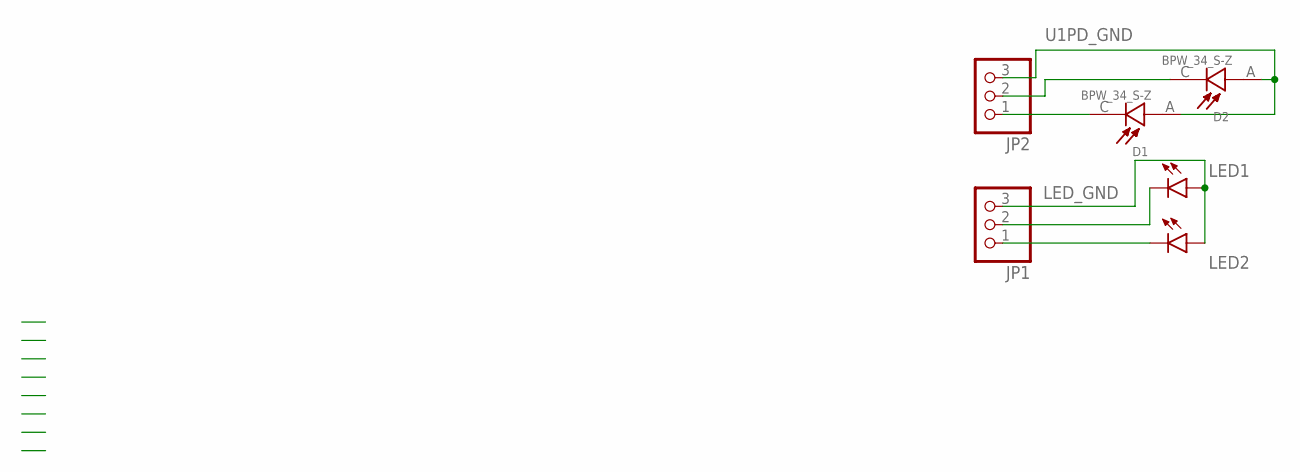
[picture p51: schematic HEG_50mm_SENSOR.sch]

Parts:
D1, D2: BPW_34_S-Z; DIO_BPW_34_S-Z
JP1, JP2: PINHD-1X3; 1X03
LED1, LED2: LEDCHIPLED_1206; CHIPLED_1206

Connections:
LED_GND: JP1.3, LED1.A, LED2.A
unnamed: JP1.1, LED2.C
unnamed: JP1.2, LED1.C
unnamed: D1.C, JP2.1
unnamed: D2.C, JP2.2
U1PD_GND: D1.A, D2.A, JP2.3

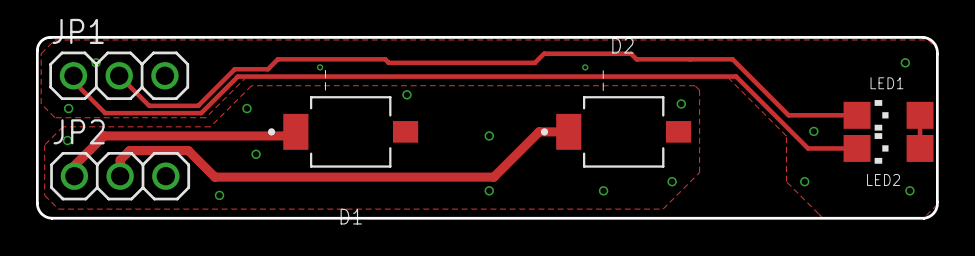
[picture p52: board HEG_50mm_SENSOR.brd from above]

Board: 2 copper layers, 50.0 x 10.1 mm, 6 parts (0 on the bottom side), 6 nets.

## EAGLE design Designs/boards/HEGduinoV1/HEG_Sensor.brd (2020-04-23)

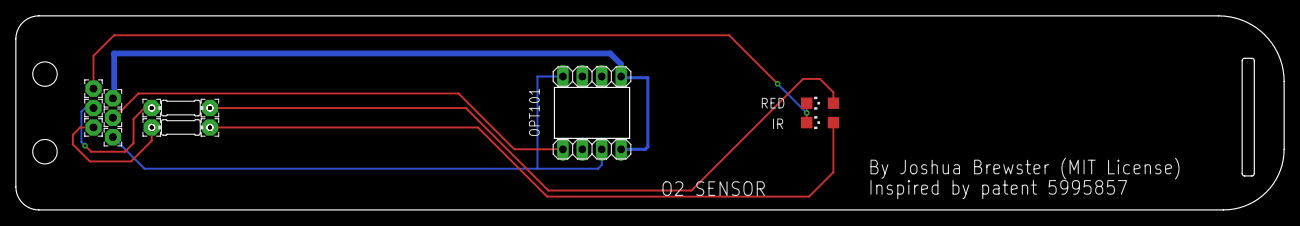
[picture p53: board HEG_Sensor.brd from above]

Board: 2 copper layers, 166.0 x 25.4 mm, 17 parts (1 on the bottom side), 4 nets.

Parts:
E$1, E$2, E$3, E$4, E$5, E$6, E$7, E$8, E$9, E$10: 2,15/1,0
IR: DN1102W; CHIPLED_1206
J1: A-2004-1-4-LP-N-R; ASSMANN_A-2004-1-4-LP-N-R
JP2: 1X04
OPT101: 1X04
R1: 470; 0204/7
R2: 62; 0204/7
RED: BR1102W; CHIPLED_1206

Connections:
AIN0: J1.5, OPT101.4
VBAT: J1.3, JP2.1
VIR: J1.2, R1.2
VRED: J1.4, R2.2

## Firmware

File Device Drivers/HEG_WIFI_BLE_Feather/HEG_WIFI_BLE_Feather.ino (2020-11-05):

//Requires these arduino libraries: Arduino ESP32 latest dev or official build via git, AsyncTCP, ESPAsyncWebServer, Arduino ADS1X15 library, ArduinoJson
//By Joshua Brewster (MIT License)
//Contributors: Diego Schmaedech and many others indirectly. 

#include "WiFi_API.h" // WiFi settings and macros. HEG and BLE libraries linked through here.

//===============================================================
// Setup
//===============================================================
bool BLEtoggle = false;
bool toggleSleep = false;
bool WIFItoggle = false;
unsigned long bootMicros = 0;


void setup(void){
  Serial.begin(115200);
  Serial.println();
  Serial.println("Booting...");

  currentMicros = esp_timer_get_time();
  setupHEG();
  delay(20);
  startADS();
  delay(20);
  EEPROM.begin(512);
  int sleep = EEPROM.read(510);
  if(sleep == 1){
    EEPROM.write(510,0); //Disarm sleep toggle for next reset
    EEPROM.end();
    Serial.println("HEG going to sleep now... Reset the power to turn device back on!");
    delay(300);
    esp_deep_sleep_start(); //Ends the loop() until device is reset.
  }
  int wifiReset = EEPROM.read(509);
  int toggle = EEPROM.read(511);
  int ComMode = EEPROM.read(0); //Communication mode (WiFi, BLE, or BT Serial)
  if(toggle == 1){
    if(ComMode == 1){
      ComMode = 0;
      EEPROM.write(0,0);
    }
    else if (ComMode == 0){
      ComMode = 2;
      EEPROM.write(0,2);
    } 
    else {
      ComMode = 1;
      EEPROM.write(0,1);
    }
  }
  EEPROM.write(510,1); //Arm the sleep toggle (first in order of checks)
  EEPROM.write(509,0); // Disarm the wifi login reset
  EEPROM.end();
  
  if(wifiReset == 1){
    saveWiFiLogin(true,false,false,false); //Reset WiFi credentials
  }

  //Now set up the communication protocols (Only 1 active at a time for best results!)
  if(ComMode == 1) {
     setupBLE();

     digitalWrite(13,HIGH);
     delay(100);
     digitalWrite(13,LOW);
     delay(100);
     digitalWrite(13,HIGH);
     delay(100);
     digitalWrite(13,LOW);
  }
  else if(ComMode == 2) {
     setupBTSerial();
     
     
     digitalWrite(13,HIGH);
     delay(100);
     digitalWrite(13,LOW);
     delay(100);
     digitalWrite(13,HIGH);
     delay(100);
     digitalWrite(13,LOW);
     delay(100);
     digitalWrite(13,HIGH);
     delay(100);
     digitalWrite(13,LOW);
     delay(100);
     digitalWrite(13,HIGH);
     delay(100);
     digitalWrite(13,LOW);
    
    
  }
  else if(ComMode == 3) {
    Serial.println("USB Only configuration.");
    Serial.println("Sample commands: 't': Toggle HEG program ON, 'f': Toggle HEG program OFF, 'u': Toggle WiFi mode, 'b': Toggle BLE mode, 'B': Toggle Bluetooth Serial mode");
  }
  else {
    setupWiFi();
    
    digitalWrite(13,HIGH);
    delay(100);
    digitalWrite(13,LOW);
    delay(100);
    digitalWrite(13,HIGH);
    delay(100);
    digitalWrite(13,LOW);
    delay(100);
    digitalWrite(13,HIGH);
    delay(100);
    digitalWrite(13,LOW);
    
  }
  bootMicros = esp_timer_get_time();
  //xTaskCreate(HEG_core_loop, "HEG_core_loop", 16384, NULL, 1, NULL);
}

void toggleCheck(){ //Checks toggles on initialization
  if(currentMicros - bootMicros < 3500000){
    if((toggleSleep == false) && (currentMicros - bootMicros > 1000000)){
      EEPROM.begin(512);
      EEPROM.write(510,0); // Disarm the sleep toggle
      EEPROM.write(511,1); // Now arm the BLE/WiFi toggle
      EEPROM.end();
      toggleSleep = true;
      
      digitalWrite(13,HIGH);
      delay(200);
      digitalWrite(13,LOW);
      
    }
    if((toggleSleep == true) && (BLEtoggle == false) && (currentMicros - bootMicros > 2000000) ){
      EEPROM.begin(512);
      EEPROM.write(511,0); //Disarm BLE/WiFi toggle
      EEPROM.write(509,1); // Now arm the Wifi reset toggle
      EEPROM.end();
      BLEtoggle = true;

      digitalWrite(13,HIGH);
      delay(200);
      digitalWrite(13,LOW);
      ;
      
    }
    if((BLEtoggle == true) && (WIFItoggle == false) && (currentMicros - bootMicros > 3000000) ){
      EEPROM.begin(512);
      EEPROM.write(509,0); //Disarm BLE/WiFi toggle
      EEPROM.end();
      WIFItoggle = true;

      digitalWrite(13,HIGH);
      delay(200);
      digitalWrite(13,LOW);
      
    }
  }
}

void checkInput()
{
  if (USE_BT == true)
  {
    while (SerialBT.available())
    {
      received = SerialBT.read();
      SerialBT.println(received);
      commandESP32(received);
      SerialBT.read(); //Flush endline for single char response
    }
  }
  if (USE_USB == true)
  {
    while (Serial.available())
    {
      received = Serial.read();
      Serial.println(received);
      commandESP32(received);
      Serial.read();
    }
  }
}

void loop(void){
  currentMicros = esp_timer_get_time();

  toggleCheck();
  
  //Serial.print("Time (ms): ");
  //Serial.println(currentMillis);
  //delayMicroseconds(500);
  HEG_core_loop();
  if(currentMicros - inputMicros >= 300000){ // Check input every N microseconds
    inputMicros = currentMicros;
    delayMicroseconds(1800);
    checkInput();
    //delayMicroseconds(1000); // Hotfix for checkInput not working without delay.
  }
}

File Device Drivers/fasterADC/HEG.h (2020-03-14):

// Joshua Brewster - HEG Arduino Functions
// Contributors - Diego Schmaedech (StateChanger Team)
// Requires Arduino ADS1x15 library and Arduino ESP32 library, as well as a compatible ESP32 board

/*
   TODO
   - Fix noise reduction, it never worked
   - HRV basic calculation, adjust LED flash rate accordingly (50ms is viable at bare min) Alternatively, get an ECG chip or use the MAX30102?
   - Accurate SpO2 reading?
   - Check power draw  
   */

#include "ADS1115.h"
//#include <Wire.h>
//#include <Adafruit_ADS1015.h>
#include <esp_timer.h>
//#include <esp_bt.h>
//#include <ArduinoJson.h>

#include "BLE_API.h"
//#include <BluetoothSerial.h>
//#include <SavLayFilter.h>

double filteredRatio;

//SavLayFilter smallFilter(&filteredRatio, 0, 5);  //Cubic smoothing with windowsize of 5
//SavLayFilter largeFilter(&filteredRatio, 0, 25); //Cubic smoothing with windowsize of 25

//Slope variables

const int SLOPE_SIZE = 20;
int slopeCounter = 0;
float slopeArray[SLOPE_SIZE];
void setupStateChanger()
{
  for (int x = 0; x < SLOPE_SIZE; x++)
  {
    slopeArray[x] = 0;
  }
}

bool USE_USB = true;          // WRITE 'u' TO TOGGLE, CHANGE HERE TO SET DEFAULT ON POWERING THE DEVICE
bool USE_BT = false;          // WRITE 'b' TO TOGGLE.
bool pIR_MODE = false;        // SET TO TRUE OR WRITE 'p' TO DO PASSIVE INFRARED ONLY (NO RED LIGHT FOR BLOOD-OXYGEN DETECTION). RATIO IS USELESS HERE, USE ADC CHANGES AS MEASUREMENT.
bool NOISE_REDUCTION = false; // WRITE 'n' TO TOGGLE USING 4 LEDS FOR NOISE CANCELLING *EXPERIMENTAL*
bool USE_DIFF = false;        // Use differential read mode, can reduce noise.
bool USE_2_3 = false;         // Use channels 2 and 3 for differential read.
bool USE_AMBIENT = true;      // Subtract the value of an intermediate no-led reading (good in case of voltage bleeding).
bool ADC_ERR_CATCH = false;   // Resets an LED reading if it does not fall within realistic margins. Prevents errors in the filters.
bool ADC_ERR_CAUGHT = false;

bool DEBUG_ESP32 = false;
bool DEBUG_ADC = false;        // FOR USE IN A SERIAL MONITOR
bool DEBUG_LEDS = false;
bool SEND_DUMMY_VALUE = false;

bool BLE_ON, BLE_SETUP = false;

const int ledRate = 2106;      // LED flash rate (us). Can go as fast as 10ms for better heartrate visibility.
const int sampleRate = 2106;   // ADC read rate (us). ADS1115 has a max of 860sps or 1/860 * 1000 ms or 1.16ms. 
const int samplesPerRatio = 3; // Minimum number of samples per LED to accumulate before makitng a measurement. Adjust this with your LED rate so you sample across the whole flash at minimum.
const int BTRate = 100000;     // Bluetooth notify rate (us). Min rate should be 10ms, however it will hang up if the buffer is not flushing. 100ms is stable.
const int USBRate = 0;         // No need to delay USB unless on old setups.

const int nSensors = 1; // Number of sensors (for automated testing)
const int nLEDs = 1; // Number of LED pairs (for automated testing)
// LED GPIO pin definitions. Default LOLIN32 Pinout, commented values are TTGO T1 pins.
int RED = 13, IR = 12 , REDn = 15, IRn = 2; //Default LED GPIO. n values are LEDs used for noise cancelling.
int IR0 = 12;    // Default left 3cm LEDs
int RED0 = 13; //33
int IR1 = 15;//15              // Left 1cm LEDs
int RED1 = 18;//2
int IR2 = 26;             // Right 1cm LEDs
int RED2 = 27;
int IR3 = 19;             // Right 3cm LEDs
int RED3 = 12;

float scaling = 1;

const int LED = 5;  // Lolin32 V1.0.0 LED on Pin 5
//const int PWR = 14;//21; // Powers ADC and OPT101

//SET NON-DEFAULT SDA AND SCL PINS
#define SDA0_PIN 23 //5
#define SCL0_PIN 19 //18

//For dual i2c or i2c switching
//#define SDA1_PIN ?
//#define SCL1_PIN ?

// HEG VARIABLES
bool coreProgramEnabled = false;
bool adcEnabled = false;
bool reset = false;
bool deviceConnected= false;

String output = "";

int16_t adc0 = 0; // Resulting 15 bit integer.
int16_t lastRead = 0;
int lastLED = 0; // 0 = NO LED, 1 = RED, 2 = IR

//Setup ADS1115
ADS1115 ads(ADS1115_DEFAULT_ADDRESS);
long adcChannel = 0; //Channel on the ADC to read. Default 0.

float Voltage = 0.0;
float range = 32767; // 16 bit ADC (15 bits of range)
float gain = 0.256;  // +/- V
float bits2mv = gain / range;

//Signal flags
bool red_led = false; // Bools to alternate LEDS
bool ir_led = false;
bool no_led = true;            // Both LEDS begin off so default is true
bool badSignal = false;        // Bool for too high of an ADC reading
bool signalDetermined = false; // Bool for whether the ADC reading is within desired range

//Counters
int ticks0 = 0, redTicks = 0, irTicks = 0, ratioTicks = 0, noiseTicks = 0, adcTicks = 0, noLEDTicks = 0;

//Scoring variables
long redValue = 0, irValue = 0, rawValue = 0;
float redGet = 0, irGet = 0, redAvg = 0, irAvg = 0, rawAvg = 0, lastRed = 0, lastIR = 0, lastRaw = 0, ratio = 0, baseline = 0;

float lastRatio = 0, v1 = 0, v2 = 0, accel = 0;
float ratioAvg = 0, adcAvg = 0, velAvg = 0, accelAvg = 0;

//TX Variables
//char adcString[10], ratioString[10], posString[10], txString[40]; // Faster in BLE mode
//char scoreString[10]

//Timing variables
unsigned long sampleMicros;
unsigned long currentMicros;
unsigned long LEDMicros;
unsigned long BLEMicros;
unsigned long USBMicros;

class MyServerCallbacks : public BLEServerCallbacks
{
  void onConnect(BLEServer *pServer)
  {
    Serial.println("Device connected to BLE");
    deviceConnected = true;
  }

  void onDisconnect(BLEServer *pServer)
  {
    Serial.println("Device disconnected from BLE");
    deviceConnected = false;
  }
};

class MyCallbacks : public BLECharacteristicCallbacks
{
  void onWrite(BLECharacteristic *pCharacteristic)
  {
    std::string rxValue = pCharacteristic->getValue();

    if (rxValue.length() > 0)
    {

      Serial.println("HEG RECEIVE: ");

      for (int i = 0; i < rxValue.length(); i++)
      {
        Serial.print(rxValue[i]);
      }
       
      //commandESP32(rxValue.c_str());

     if (rxValue.find("t") != -1)
      { 
        coreProgramEnabled = true;
        Serial.println("Turning ON!");
        reset=true;
        //digitalWrite(LED, LOW); // LOLIN32 Indicator LED
      }
      else if (rxValue.find("f") != -1)
      {
        Serial.println("Turning OFF!");
        coreProgramEnabled = false;
        delay(300);
        //digitalWrite(LED, HIGH); // LOLIN32 Indicator LED
        digitalWrite(RED, LOW);
        digitalWrite(IR, LOW);
        no_led = true;
        red_led = false;
        ir_led = false;
        reset = true;
      }
      else if (rxValue.find("b") != -1)
      {
        EEPROM.begin(512);
        if (EEPROM.read(0) == 0)
        {
          EEPROM.write(0,1);
          EEPROM.commit();
          EEPROM.end();
          delay(100);
          ESP.restart();
        }
        else
        {
          EEPROM.write(0,0);
          EEPROM.commit();
          EEPROM.end();
          delay(100);
          ESP.restart();
        }
      }
      else if (rxValue.find("R") != -1) {
        delay(300);
        ESP.restart();
      }
    }
  }
};

void setupBLE(){

    // Create the BLE Device
    BLEDevice::init("My_HEG"); // Give it a name
    BLEDevice::setMTU(512);

    // Create the BLE Server
    BLEServer *pServer = BLEDevice::createServer();
    pServer->setCallbacks(new MyServerCallbacks());

    // Create the BLE Service
    BLEService *pService = pServer->createService(SERVICE_UUID);

    // Create a BLE Characteristic
    pCharacteristic = pService->createCharacteristic(CHARACTERISTIC_UUID_TX, BLECharacteristic::PROPERTY_NOTIFY);

    BLE2902 *desc = new BLE2902();
    desc->setNotifications(true);
    pCharacteristic->addDescriptor(desc);

    pCharacteristic = pService->createCharacteristic(CHARACTERISTIC_UUID_TX, BLECharacteristic::PROPERTY_NOTIFY | BLECharacteristic::PROPERTY_READ | BLECharacteristic::PROPERTY_WRITE);
    pCharacteristic->setReadProperty(true);
    pCharacteristic->setCallbacks(new MyCallbacks());

    // Start the service
    pService->start();

    // Start advertising
    pServer->getAdvertising()->start();
    BLE_SETUP = true;
    BLE_ON = true;
    USE_BT = true;
    Serial.println("BLE service started, scan for My_HEG.");
}


void readADC(){
  //delayMicroseconds(sampleRate); //Delay so you know a sample happened during a given cycle(on continuous mode)
  lastRead = adc0;
  if(USE_DIFF == false){
    if(adcChannel == 0){
      adc0 = ads.getConversionP0GND();
    }
    if(adcChannel == 1){
      adc0 = ads.getConversionP1GND();
    }
    if(adcChannel == 2){
      adc0 = ads.getConversionP2GND();
    }
    if(adcChannel == 3){
      adc0 = ads.getConversionP3GND();
    }
    //adc0 = ads.readADC_SingleEnded(adcChannel); // -1 indicates something wrong with the ADC (usually pin settings or solder)
  }
  else{
    if(USE_2_3 == false){
      adc0 = ads.getConversionP0N1();
    }
    else {
      adc0 = ads.getConversionP2N3();
    }
  }
  sampleMicros = esp_timer_get_time();
}

void setMux() {
  if(USE_DIFF == false){
    if(adcChannel == 0){
      ads.setMultiplexer(ADS1115_MUX_P0_NG);
    }
    if(adcChannel == 1){
      ads.setMultiplexer(ADS1115_MUX_P1_NG);
    }
    if(adcChannel == 2){
      ads.setMultiplexer(ADS1115_MUX_P2_NG);
    }
    if(adcChannel == 3){
      ads.setMultiplexer(ADS1115_MUX_P3_NG);
    }
  }
  else{
    if(USE_2_3 == false){
      ads.setMultiplexer(ADS1115_MUX_P0_N1);
    }
    else{
      ads.setMultiplexer(ADS1115_MUX_P2_N3);
    }
  }
    //Voltage = (adc0 * bits2mv);
  

}
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

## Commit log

2019-01-24 use this
    added reset command (send 'r' to device to reset the baseline)
2019-01-24 custom prototype progress
2019-02-12 Made IR and RED LED pins match code.
2019-03-07 updated arduino profile and studio
    quite a few changes and rearrangements.
    You can switch ADC pins by sending '0' thru '3' to the device.
    Resolved the LED sampling, was slightly off sync
2019-03-18 added whitepaper (with code walkthrough), custom SDA/SCL pin code
2019-05-24 fixed LED timers
    code will get major changes soon including output format
2019-09-13 New WiFi mode with BLE switch.
    Requires some changes to default ESP32 templates, see readme.
    temp: HEGstudio compatibility broken
    [default.csv]
2019-09-13 update pin definitions
2019-10-22 add suggest IP option to test for a static IP if esp32.local does not work.
2019-11-09 Removed sav lay filter and changed programs to match (just need to recompile hegstudio)
2019-12-04 Sensor is FAST, but requires new libs. Updated help and added a compiled .bin for this version (upload via /update)
2019-12-11 fixed gpio, fixed sampling, need to address power supply
2019-12-12 added replay data that shows acceptable results
    [good1.csv, good2.csv]
2020-01-23 big updates
    [default.csv, good1.csv, good2.csv]
2020-01-23 moved some stuff
    [good1.csv, good2.csv]
2020-01-30 updated assembly guide, help pages WIP
2020-02-13 exposed event source hosting option (for clients not hosted on-board but connected to same network)
2020-02-27 fixes and tweaks
    [bad_butusable(old).csv, okay_witherrors(old).csv]
2020-02-27 Moved files, added quick data analyzer html interface
    [bad_butusable(old).csv, default.csv, okay_witherrors(old).csv]
2020-03-03 updated, fixed annotations, more recent sample data
    [bad_butusable(old).csv, okay_witherrors(old).csv, sample1.csv]
2020-03-03 updated webapi SMA function, added basic fault testing for ratio (keeps within 25% error)
    [prettygood.csv, session_yeah.csv, wiggle_forehead.csv]
2020-03-09 Added a folder of the additional dependencies for Arduino and ESP32
2020-03-18 added boards
    [ESP32_ADC_HUB.brd, HEG_Sensor.brd]
2020-03-22 moved stuff
    [ESP32_ADC_HUB.brd, HEG_Sensor.brd, default.csv]
2020-03-23 slight camera tweak
2020-03-23 updated diagrams in assembly guide and a few descriptions for clarity
2020-03-24 rebuilt bins just in case of issues, also fixes the update progress bar
2020-03-26 fixed, added deep sleep mode (for battery saving)
2020-04-04 changed 'u' command to toggle USB-only mode (no wireless coms), fixed autoscale issue
2020-04-23 Added some sensor designs, moved some stuff
    [ESP32_ADC_HUB.brd, HEG_50mm_SENSOR.brd, HEG_50mm_SENSOR.sch, HEG_Sensor.brd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]
2020-05-08 updated HEG schematic (1.1, testing it)
    [ESP32_ADC_HUB.brd, ESP32_ADC_HUB.sch, copper_bottom.gbr, copper_top.gbr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]
2020-05-08 hegduino 1.1 brd
    [ESP32_ADC_HUB.sch]
2020-05-08 uploaded canned designs (be freeeeee!!!)
    [HEG-MAX30112-BOM.xlsx, MAX86141HEG_BOM.xls]
2020-05-09 upload schematic
    [AD7771Breakout.sch]
2020-05-09 update schematic
    [AD7771Breakout.sch]
2020-05-18 updated advanced design (need to test)
    [MAX86141HEG_BOM.xls, MAX86141_HEG_MINI.brd, MAX86141_HEG_MINI.sch]
2020-05-26 0.0.9 update
    [MAX86141HEG_BOM.xls, MAX86141_HEG_MINI.brd]
2020-06-02 tweaks and fixes, lower power consumption on LOLIN32, brd updates
    [AD7771Breakout.sch, ESP32_ADC_HUB.brd, ESP32_ADC_HUB.sch, HEG-MAX30112-BOM.xlsx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]
2020-06-08 updated assembly guide
2020-07-16 updated webAPI, device stream format compatibility controllable via one liners and commands now. custom firmware now easier
    [MAX86141HEG_BOM.xls, MAX86141_HEG_MINI.brd]
2020-07-19 moved js files, testing gpu.js
    [MAX86141_HEG_MINI_centroid.csv]
2020-10-20 lolin32 firmware should update properly now
    [MAX86141HEG_BOM.xls, MAX86141_HEG_MINI.brd, MAX86141_HEG_MINI.sch, MAX86141_HEG_MINI_HEADPIECE.brd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]
2020-10-31 boids update on boards 0.1.12 update
2020-11-06 reupload feather bin (just in case I compiled it wrong)
2021-01-22 implement IIR filters (let me know if they help)
2021-02-08 rollback while fixing filters.

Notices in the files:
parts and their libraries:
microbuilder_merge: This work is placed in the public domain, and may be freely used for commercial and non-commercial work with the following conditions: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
